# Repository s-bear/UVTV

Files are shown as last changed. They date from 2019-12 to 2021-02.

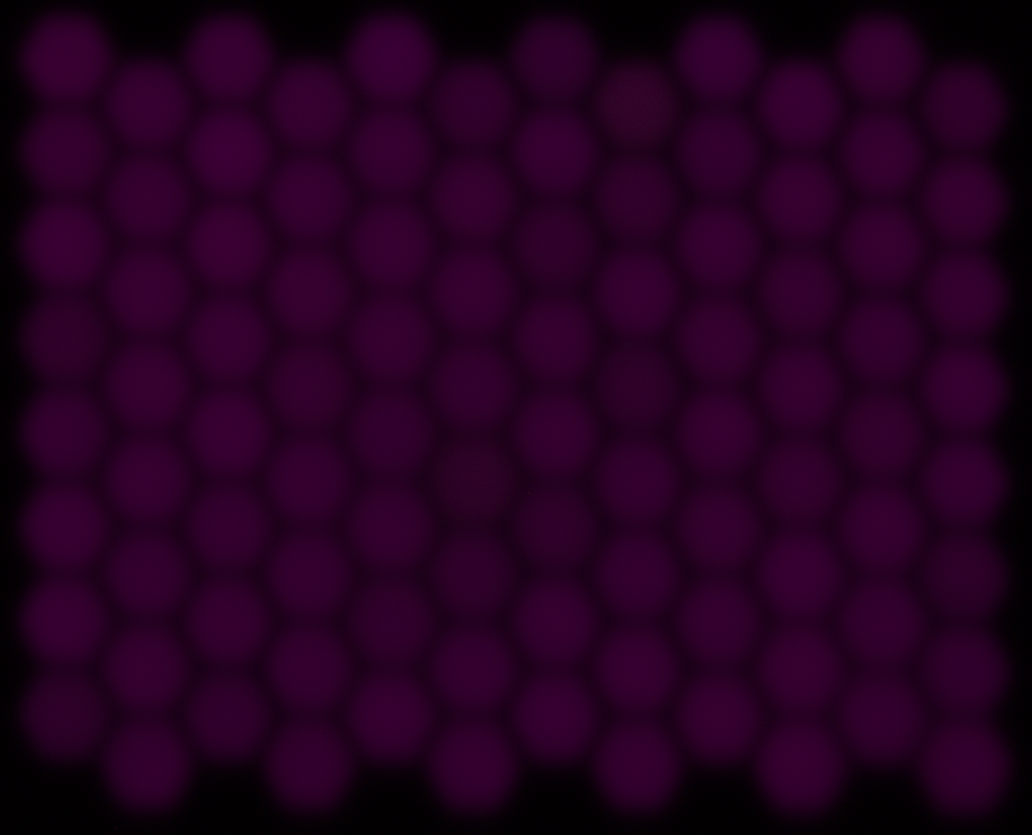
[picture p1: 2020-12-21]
software/scripts/board 2 data/uv_0.png

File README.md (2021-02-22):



# UVTV
RGB-V-UV LED display, as published in "A five-channel LED display to investigate UV perception" in Methods in Ecology and Evolution, 2021.

## TO DO
- Display: Compactness and seamless edge-to-edge display panelling is *not* a priority any more. There are a few places where these design goals made things quite difficult and any new production should have these changes made:
  - [ ] Point-of-Load power supply on display board for LEDs.
  - [ ] Separate LED power from TLC5955 power.
  - [ ] Increase margins and put mounting holes in sane places.
  - [ ] Use larger connectors for the flat-flex cables. Assess signal integrity and see if more conductors would be useful for shielding.
  - [ ] Another layer of PCB might be in order to ease routing of control signals, especially if there are signal integrity issues at higher speeds.
- Controller: A higher-speed controller is necessary to use the full potential of the display panel. There are several viable alternatives:
  1. A high-speed microcontroller module, such as the Teensy 4.1 (600 MHz), using built-in SPI or bit-banging to communicate with TLC5955 chips.
  2. A microcontroller + FPGA combo -- using the microcontroller to handle USB and FPGA to handle the TLC5955 communication.
  3. An FPGA to handle both USB and TLC5955.
- 3D Models
  - [ ] Redraw in an open source CAD tool, e.g. FreeCAD.

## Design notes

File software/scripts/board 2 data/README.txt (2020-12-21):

This is example flatfield calibration data from the 2nd UVTV board made.

The directories 0, 1, and 2 hold data captured before calibration (0) and 
after 1 and 2 iterations of the procedure respectively.

The "test_panel.py" script was run to show the "corners", "red", "green",
"blue", "violet", and "uv" images.
For the initial run, the script was configured with:
    reset_config = True
    save_config = False
    config_path = 'board 2 data/0'
Setting "reset_config = True" means the script generates "panel_config.npz" with
default data (lines 30-37).

Photos of the display were taken at each stage of the script using a modified
Olympus E-PL5 camera, the raw ORF files saved in 'board 2 data/0'.

The ORF files were converted to tiff using RawTherapee, with the settings
stored in the associated pp3 files. As the tiff files are too large for
github, you must generate them yourself using RawTherapee.

"pixel_stats.py" was run with
    config_path = 'board 2 data/0'
to generate "pixel_stats.npz"

"flatfield.py" was run with
    config_path = 'board 2 data/0'
to update "panel_config.npz" with new dotcorrect coefficients.

The procedure was then repeated again, running "test_panel.py" with
    reset_config = False
    save_config = False
    config_path = 'board 2 data/0'

The new images were saved into "board 2 data/1" and "0/panel_config.npz" was
copied to "1/panel_config.npz" so that "flatfield.py" could update it with new
coefficients.

The final round of images was generated using these coefficients and saved into
"board 2 data/2" for validation and to generate figures showing uniformity.

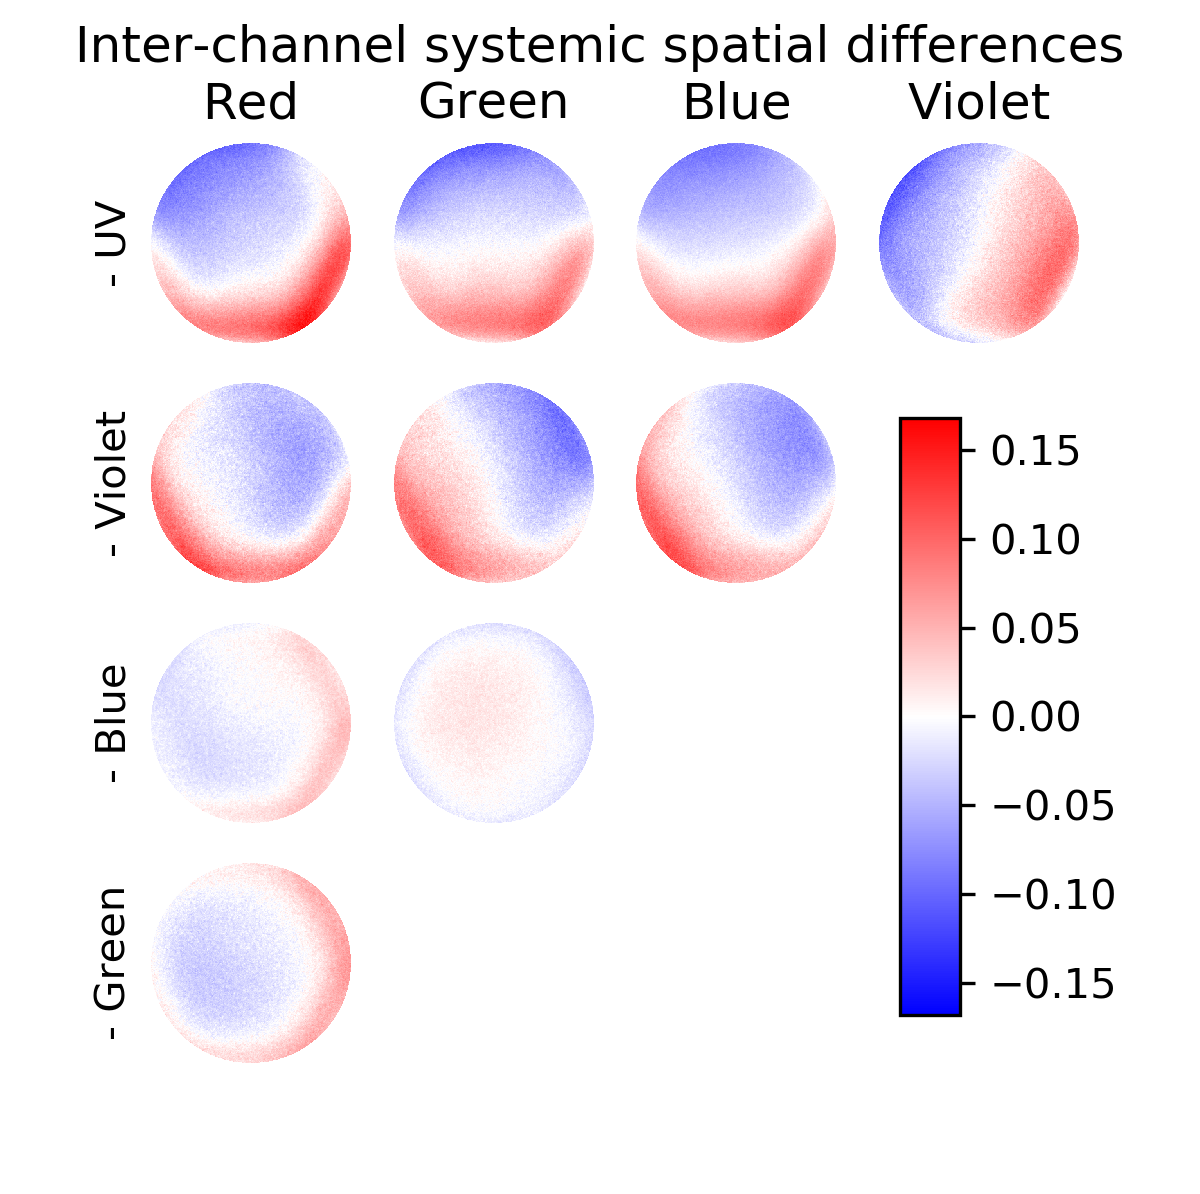
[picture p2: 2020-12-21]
software/scripts/board 2 data/spatial deviation.png

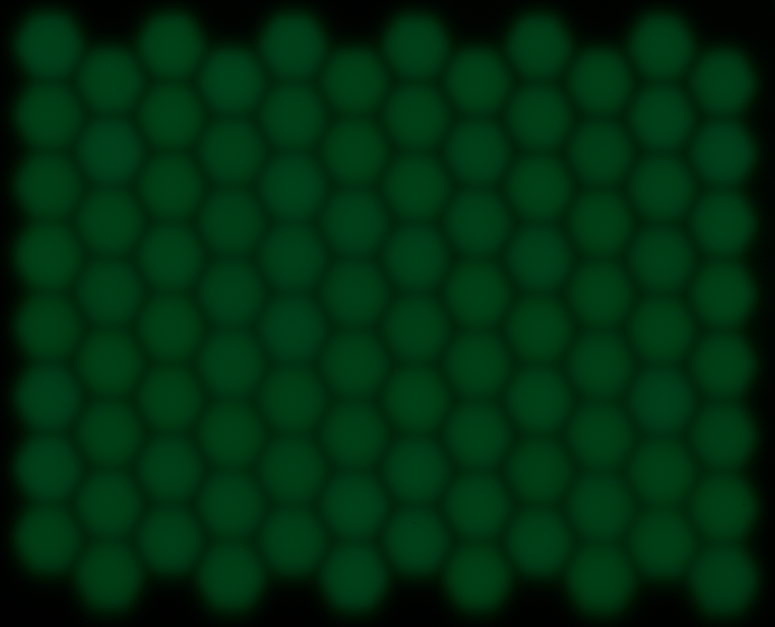
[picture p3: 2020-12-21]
software/scripts/board 2 data/green_0.png

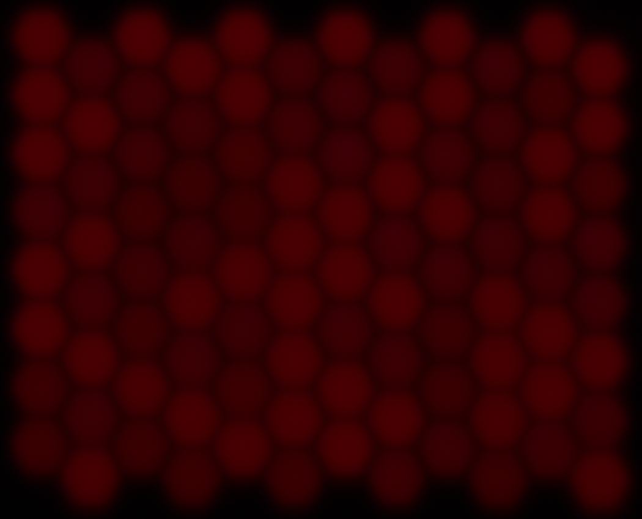
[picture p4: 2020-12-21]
software/scripts/board 2 data/red_0.png

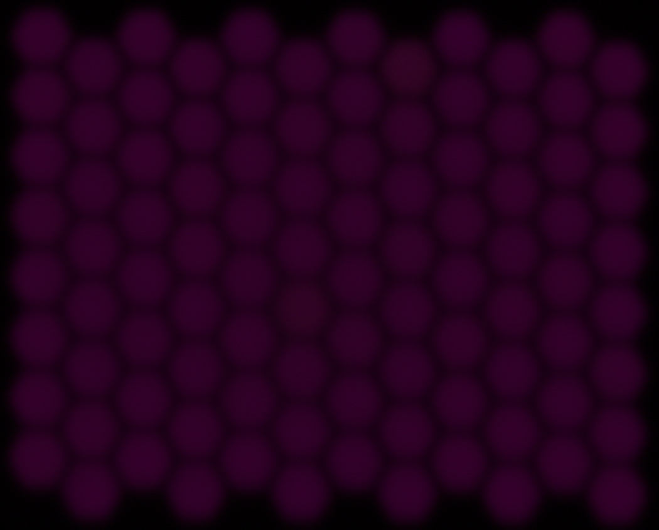
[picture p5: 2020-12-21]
software/scripts/board 2 data/uv_2.png

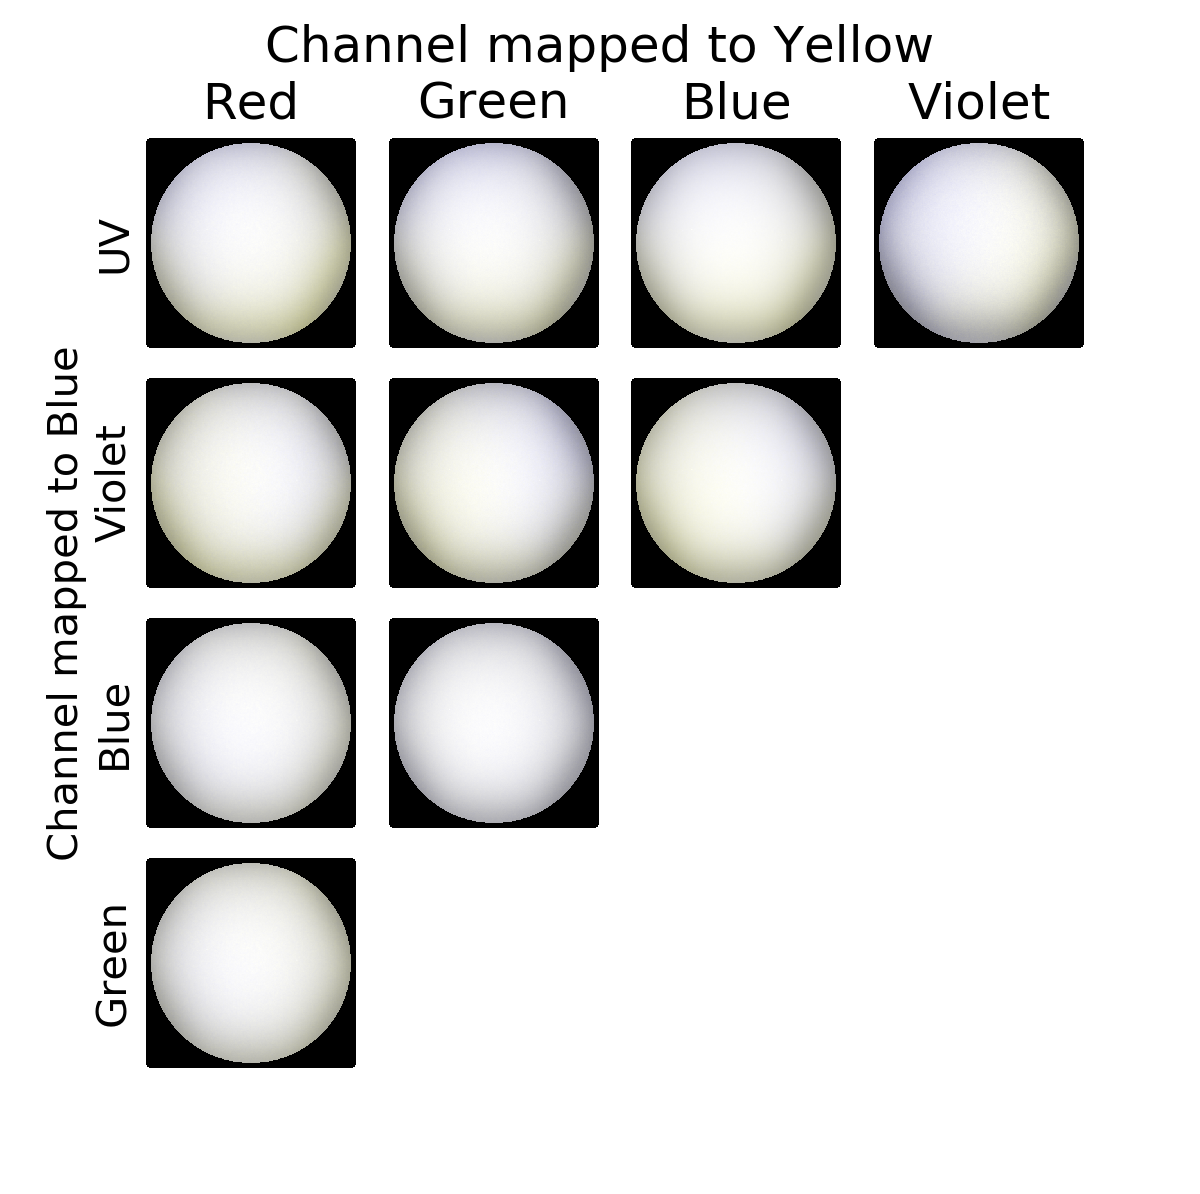
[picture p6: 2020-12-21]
software/scripts/board 2 data/spatial deviation 2.png

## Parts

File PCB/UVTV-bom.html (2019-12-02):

Ref | Count | Value | Library | Part | Footprint | Description | Vendor
C1 | 1 | 220u | Device | CP | Capacitor_Tantalum_SMD:CP_EIA-7343-31_Kemet-D_Pad2.25x2.55mm_HandSolder | Polarised capacitor
C2, C3 | 2 | 47u | Device | C | Capacitor_SMD:C_1206_3216Metric_Pad1.42x1.75mm_HandSolder | Unpolarized capacitor
C4 | 1 | 100u | Device | CP | Capacitor_Tantalum_SMD:CP_EIA-7343-31_Kemet-D_Pad2.25x2.55mm_HandSolder | Polarised capacitor
C[5:6] | 2 | 0.1u | Device | C | Capacitor_SMD:C_0603_1608Metric_Pad1.05x0.95mm_HandSolder | Unpolarized capacitor
J0 | 1 | Barrel_Jack | Connector | Barrel_Jack_MountingPin | Connector_BarrelJack:BarrelJack_CUI_PJ-063AH_Horizontal_CircularHoles | DC Barrel Jack with a mounting pin
J1 | 1 | Conn_01x08_Male | Connector | Conn_01x08_Male | Connector_PinHeader_2.54mm:PinHeader_1x08_P2.54mm_Vertical | Generic connector, single row, 01x08, script generated (kicad-library-utils/schlib/autogen/connector/)
Q0[A:B], Q1[A:B] | 4 | Q_NMOS_GSD | Device | Q_NMOS_GSD | Package_TO_SOT_SMD:SOT-23 | Transistor N-MOSFETwith substrate diode (general)
R1 | 1 | 348k | Device | R | Resistor_SMD:R_0603_1608Metric_Pad1.05x0.95mm_HandSolder | Resistor
R2 | 1 | 422 | Device | R | Resistor_SMD:R_0603_1608Metric_Pad1.05x0.95mm_HandSolder | Resistor
R[3:12] | 10 | 12Ω, 1W | Device | R | Resistor_THT:R_Axial_DIN0207_L6.3mm_D2.5mm_P10.16mm_Horizontal | Resistor
RGB[0:15] | 16 | LED_ARGB | Device | LED_ARGB | UVTV:EAST1616RGBA | LED RGB, common anode (pin 1)
U0 | 1 | LMZ3060x | UVTV | LMZ3060x | UVTV:Ti-S-PB1QFN-N39
U[1:2] | 2 | TLC5955-DCA | UVTV | TLC5955-DCA | Package_SO:HTSSOP-56-1EP_6.1x14mm_P0.5mm_EP3.61x6.35mm
UV[0:15] | 16 | LED | Device | LED | UVTV:D_0606_1616Metric | LED generic
V[0:15] | 16 | LED | Device | LED | LED_SMD:LED_0603_1608Metric | LED generic

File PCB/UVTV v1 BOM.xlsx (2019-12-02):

Source | G:\Sam\Projects\UV LED display\UVTV\UVTV.sch
Date | 2019-05-17
Tool | Eeschema (5.0.1)-3
Component count | 311
Ref | Count | Value | Voltage | Description | Manufacturer | Part # | Vendor | Order # | Note
~ | 1 |  |  | FFC cable 0.5mm, 15 POS, 152 mm long | Parlex USA LLC | 050R15-152B | Digikey | HFF-15U-06 | Other brands acceptable, length within 120-200 mm
C1A,C1B,C1C,C1D,C1E,C2A,C2B,C2C,C2D,C2E | 10 | 0.1u | 6V | Decoupling caps | Samsung | CL10F104ZO8NNNC | Digikey | 1276-1258 | Other brands acceptable
J1 | 1 |  |  | FFC connector | Hirose | FH19SC-15S-0.5SH(09) | Digikey | H125831
RGB1A0,RGB1A1,RGB1A2,RGB1A3,RGB1A4,RGB1A5,RGB1A6,RGB1A7,RGB1A8,RGB1A9,RGB1A10,RGB1A11,RGB1A12,RGB1A13,RGB1A14,RGB1A15,RGB1B0,RGB1B1,RGB1B2,RGB1B3,RGB1B4,RGB1B5,RGB1B6,RGB1B7,RGB1B8,RGB1B9,RGB1B10,RGB1B11,RGB1B12,RGB1B13,RGB1B14,RGB1B15,RGB1C0,RGB1C1,RGB1C2,RGB1C3,RGB1C4,RGB1C5,RGB1C6,RGB1C7,RGB1C8,RGB1C9,RGB1C10,RGB1C11,RGB1C12,RGB1C13,RGB1C14,RGB1C15,RGB2A0,RGB2A1,RGB2A2,RGB2A3,RGB2A4,RGB2A5,RGB2A6,RGB2A7,RGB2A8,RGB2A9,RGB2A10,RGB2A11,RGB2A12,RGB2A13,RGB2A14,RGB2A15,RGB2B0,RGB2B1,RGB2B2,RGB2B3,RGB2B4,RGB2B5,RGB2B6,RGB2B7,RGB2B8,RGB2B9,RGB2B10,RGB2B11,RGB2B12,RGB2B13,RGB2B14,RGB2B15,RGB2C0,RGB2C1,RGB2C2,RGB2C3,RGB2C4,RGB2C5,RGB2C6,RGB2C7,RGB2C8,RGB2C9,RGB2C10,RGB2C11,RGB2C12,RGB2C13,RGB2C14,RGB2C15 | 96 |  |  | RGB LEDs | Everlight Electronics Co Ltd | EAST1616RGBA3 | Digikey | 1080-1550
U-RGB1A,U-RGB2A,U-RGB1B,U-RGB2B,U-RGB1C,U-RGB2C,U-UV1A,U-UV2A,U-UV1C,U-UV2C | 10 |  |  | 3x16 CC LED controller | Texas Instruments | TLC5955RTQR | Digikey | 296-40588
UV1A0,UV1A1,UV1A2,UV1A3,UV1A4,UV1A5,UV1A6,UV1A7,UV1A8,UV1A9,UV1A10,UV1A11,UV1A12,UV1A13,UV1A14,UV1A15,UV1B0,UV1B1,UV1B2,UV1B3,UV1B4,UV1B5,UV1B6,UV1B7,UV1B8,UV1B9,UV1B10,UV1B11,UV1B12,UV1B13,UV1B14,UV1B15,UV1C0,UV1C1,UV1C2,UV1C3,UV1C4,UV1C5,UV1C6,UV1C7,UV1C8,UV1C9,UV1C10,UV1C11,UV1C12,UV1C13,UV1C14,UV1C15,UV2A0,UV2A1,UV2A2,UV2A3,UV2A4,UV2A5,UV2A6,UV2A7,UV2A8,UV2A9,UV2A10,UV2A11,UV2A12,UV2A13,UV2A14,UV2A15,UV2B0,UV2B1,UV2B2,UV2B3,UV2B4,UV2B5,UV2B6,UV2B7,UV2B8,UV2B9,UV2B10,UV2B11,UV2B12,UV2B13,UV2B14,UV2B15,UV2C0,UV2C1,UV2C2,UV2C3,UV2C4,UV2C5,UV2C6,UV2C7,UV2C8,UV2C9,UV2C10,UV2C11,UV2C12,UV2C13,UV2C14,UV2C15 | 96 |  |  | UV LED (365 nm) | Vishay Semiconductor Opto Division | VLMU1610-365-135 | Digikey | VLMU1610-365-135
V1A0,V1A1,V1A2,V1A3,V1A4,V1A5,V1A6,V1A7,V1A8,V1A9,V1A10,V1A11,V1A12,V1A13,V1A14,V1A15,V1B0,V1B1,V1B2,V1B3,V1B4,V1B5,V1B6,V1B7,V1B8,V1B9,V1B10,V1B11,V1B12,V1B13,V1B14,V1B15,V1C0,V1C1,V1C2,V1C3,V1C4,V1C5,V1C6,V1C7,V1C8,V1C9,V1C10,V1C11,V1C12,V1C13,V1C14,V1C15,V2A0,V2A1,V2A2,V2A3,V2A4,V2A5,V2A6,V2A7,V2A8,V2A9,V2A10,V2A11,V2A12,V2A13,V2A14,V2A15,V2B0,V2B1,V2B2,V2B3,V2B4,V2B5,V2B6,V2B7,V2B8,V2B9,V2B10,V2B11,V2B12,V2B13,V2B14,V2B15,V2C0,V2C1,V2C2,V2C3,V2C4,V2C5,V2C6,V2C7,V2C8,V2C9,V2C10,V2C11,V2C12,V2C13,V2C14,V2C15 | 96 |  |  | UV LED (395 nm) | Bivar Inc | SM0603UV-395 | Digikey | 492-1949

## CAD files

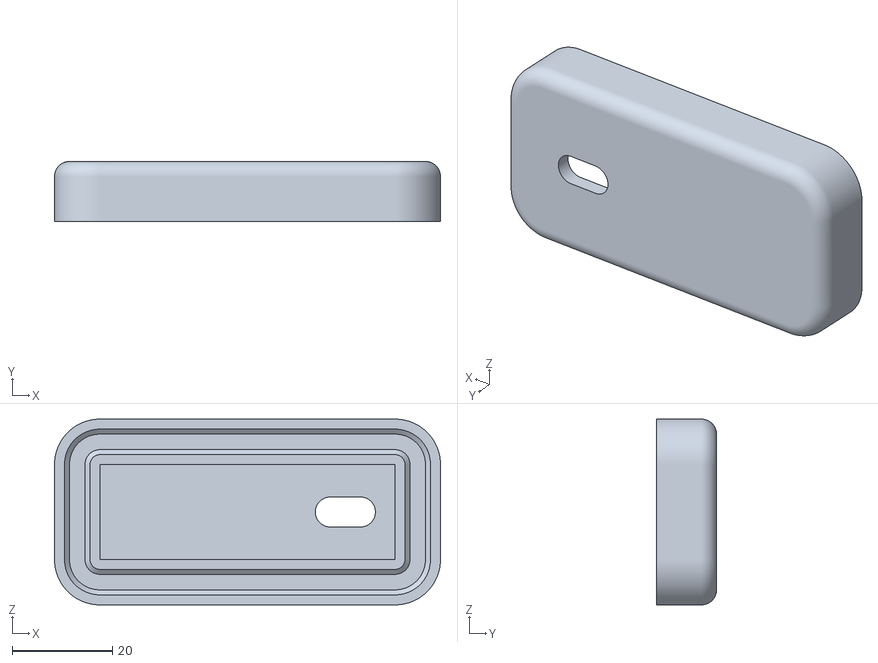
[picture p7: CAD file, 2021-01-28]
3D models/LED box top.stl
77.1 x 12.0 x 37.1

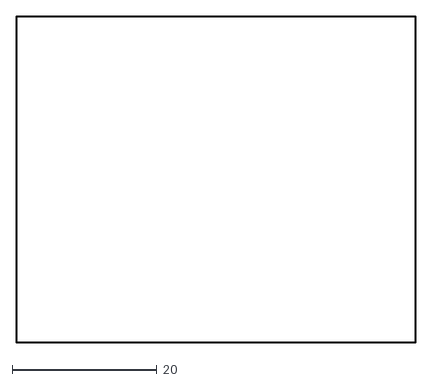
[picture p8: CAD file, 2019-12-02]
PCB/Gerbers/UVTV-Edge.Cuts.dxf
55.1 x 45.1

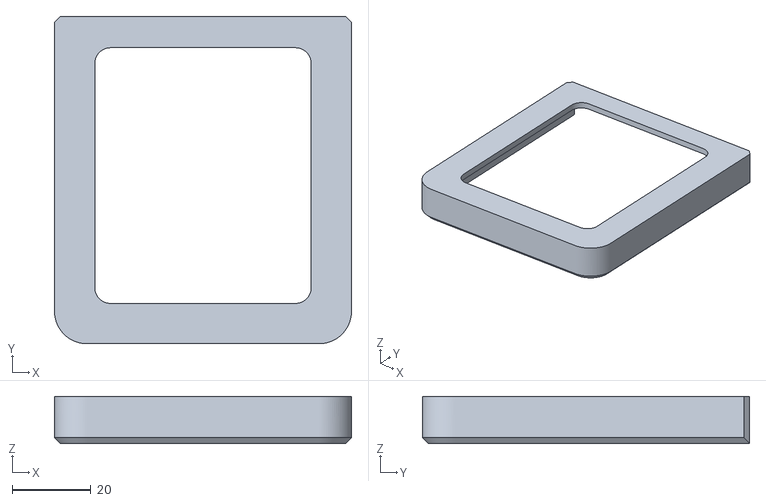
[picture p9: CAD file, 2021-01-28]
3D models/LED box bracket.stl
75.5 x 83.2 x 12.0

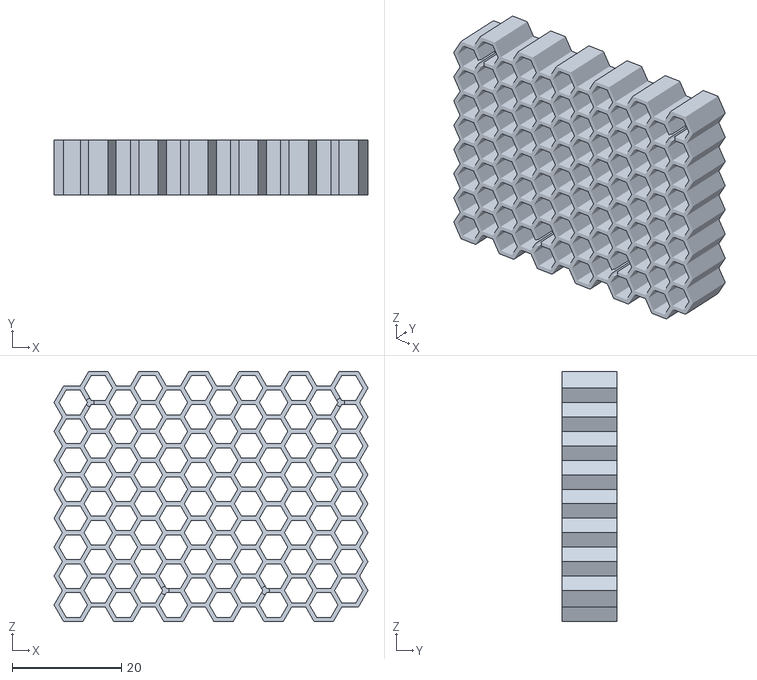
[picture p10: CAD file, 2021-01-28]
3D models/baffle.stl
57.5 x 10.0 x 45.8

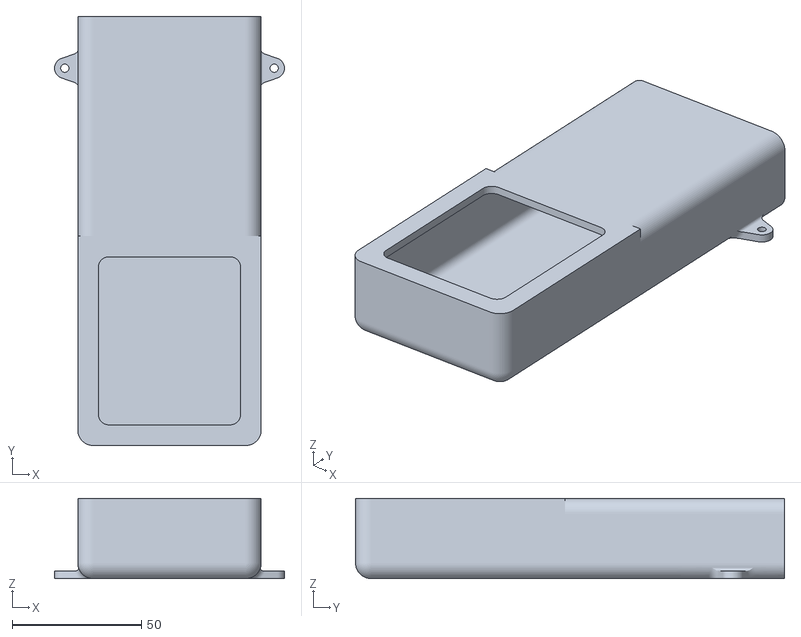
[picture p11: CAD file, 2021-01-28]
3D models/LED box.stl
89.0 x 166.0 x 31.0

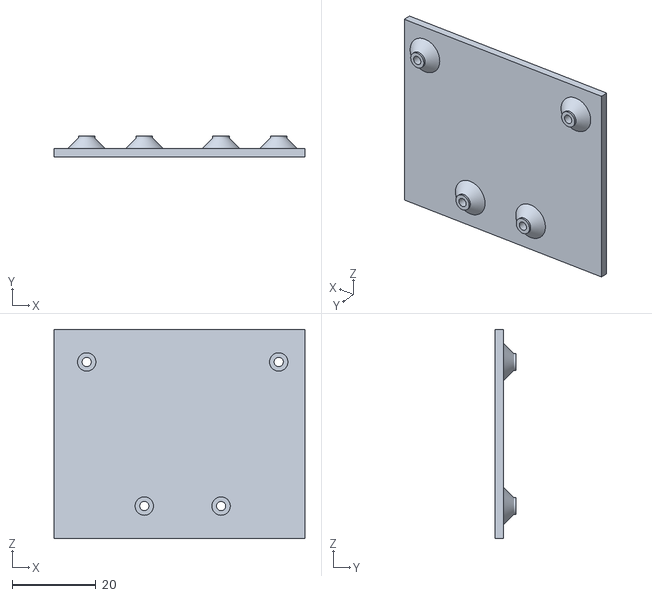
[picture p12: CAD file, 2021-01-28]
3D models/Panel mount plate.stl
60.0 x 5.00 x 50.0

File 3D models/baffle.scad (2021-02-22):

$fs = 0.1;

pitch = 5.3;
grid = [12,8];
wall = 0.8;
height = 10;

hole_dia = 1.5;
hole_depth = 5;

pitch_x = pitch*cos(30);
cell_w = pitch/cos(30);

hole_offsets = [
        [3*pitch_x + 0.5*cell_w, pitch/2],
        [7*pitch_x + 0.5*cell_w, pitch/2],
        [0.5*cell_w, 7*pitch],
        [10*pitch_x + 0.5*cell_w, 7*pitch]
    ];

module cylinder_outer(height,radius) {
    n = ($fn>0?($fn>=3?$fn:3):ceil(max(min(360/$fa,radius*2*PI/$fs),5)));
    cylinder(h=height,r=radius/cos(180/n),$fn=n);
}

module hex(h,w) {
    //w is across flats
    r = w*0.5773502691896257; // 1/(2*cos(180/6))
    cylinder(h,r,r,$fn=6);
}

module cell() {
    difference() {
        hex(height,pitch+wall);
        hex(height,pitch-wall);
    }
}

difference() {
    union() {
        for(ix = [0 : 2 : grid.x - 1]) {
            for(iy = [0 : grid.y - 1]) {
                translate([pitch_x*ix, pitch*iy]) cell();
                translate([pitch_x*(ix+1),pitch*(iy+0.5)]) cell();
            }
        }
    }

    for(xy = hole_offsets) {
        translate(xy)
        cylinder_outer(hole_depth,hole_dia/2);
    }
}

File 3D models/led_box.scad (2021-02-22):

$fs = 0.1;
tolerance = 1; //gap between parts

//main body parameters
window_size = [55,65];
interior_depth = 25;
flat_width = 10;
wall_thickness = 3;
tube_length = 85;

hole_offset = 20;
hole_pad_dia = 8;
hole_dia = 3.2;
tab_thickness = 5;

window_fillet = 3;
interior_fillet = 3;

//lid
lid_slot = [10, 15]; //diameter, length
lid_lip = 5;

//retainer
retainer_lip = 10;

//platform
platform_size = [50,60];
standoff_dia = 4;
platform_hole = [2.2,4.4,1.6]; //diameter, countersink diameter, countersink depth

pitch = 5.3;
grid = [8,12];

//computed parameters
exterior_fillet = interior_fillet+wall_thickness;
box_size = [window_size.x + 2*flat_width, window_size.y + 2*flat_width, interior_depth + 2*wall_thickness];
tube_size = [window_size.x+2*flat_width,interior_depth+2*wall_thickness,tube_length];

lid_size = [tube_size.x + 2*wall_thickness + tolerance, tube_size.y + 2*wall_thickness + tolerance, lid_lip + wall_thickness];
lid_fillet = exterior_fillet + wall_thickness + tolerance/2;

module square_rounded(size, radius, center = false) {
    offset(r = radius) {
        offset(delta = -radius) {
            square(size,center);
        }
    }
}

//from https://en.wikibooks.org/wiki/OpenSCAD_User_Manual/Other_Language_Features
function circle_edges(r) = ($fn>0?($fn>=3?$fn:3):ceil(max(min(360/$fa,r*2*PI/$fs),5)));

module circle_outer(radius) {
    //number of edges
    n = circle_edges(radius);
    circle(r=radius/cos(180/n),$fn=n);
}

module cylinder_outer(height,radius) {
    n = circle_edges(radius);
    cylinder(h=height,r=radius/cos(180/n),$fn=n);
}

module cube_rounded(size, radius) {
    dx = size.x/2 - radius;
    dy = size.y/2 - radius;
    dz = size.z/2 - radius;
    hull() {
        translate([-dx,-dy,-dz]) sphere(radius);
        translate([ dx,-dy,-dz]) sphere(radius);
        translate([-dx, dy,-dz]) sphere(radius);
        translate([ dx, dy,-dz]) sphere(radius);
        translate([-dx,-dy, dz]) sphere(radius);
        translate([ dx,-dy, dz]) sphere(radius);
        translate([-dx, dy, dz]) sphere(radius);
        translate([ dx, dy, dz]) sphere(radius);
    };
}

module window_box_shell(size, radius) {
    hull() {
        dx = size.x/2 - radius;
        dy = size.y/2 - radius;
        dz = size.z/2 - radius;
        translate([-dx,-dy,-dz]) sphere(radius);
        translate([ dx,-dy,-dz]) sphere(radius);
        translate([-dx, dy,-dz]) rotate([90,0,0]) cylinder(2*radius,r=radius,center=true);
        translate([ dx, dy,-dz]) rotate([90,0,0]) cylinder(2*radius,r=radius,center=true);
        translate([-dx,-dy, dz]) cylinder(2*radius,r=radius,center=true);
        translate([ dx,-dy, dz]) cylinder(2*radius,r=radius,center=true);
        translate([-dx, dy, dz]) rotate([90,0,0]) cube(2*radius,center=true);
        translate([ dx, dy, dz]) rotate([90,0,0]) cube(2*radius,center=true);
    };    
}


module window_box() {
    difference() {
        //outer shell
        window_box_shell(box_size, interior_fillet + wall_thickness);
        
        //cut away interior to leave walls
        translate([0,wall_thickness,0])
        cube_rounded(box_size - [2*wall_thickness,0,2*wall_thickness], interior_fillet);
        
        //cut the window out
        translate([0,0,box_size.z/2 - 0.5*wall_thickness])
        linear_extrude(1.1*wall_thickness,center=true) {
           square_rounded(window_size,window_fillet,true);
        }
    }
}

module mount_tab(x) {
    translate([x,0,0])
    difference() {
    //rounded triangle
        linear_extrude(tab_thickness) {
            translate([-hole_pad_dia,0,0])
            minkowski() {
                circle(d=hole_pad_dia);
                circle(d=2*hole_pad_dia, $fn=3);
            }
        }
        translate([0,0,-0.05])
        cylinder_outer(1.1*tab_thickness,hole_dia/2);
    }
}


module tube() {
    difference() {
        union() {
            //tube body
            linear_extrude(tube_size.z)
            square_rounded([tube_size.x,tube_size.y],exterior_fillet,center=true);
    
            translate([0, tube_size.y/2, tube_length - hole_offset]) rotate([90,0,0]) {
                mount_tab(tube_size.x/2 + hole_pad_dia/2);
                mirror([1,0,0]) mount_tab(tube_size.x/2 + hole_pad_dia/2);
            }
        }
        //remove tube interior
        translate([0,0,-0.05])
        linear_extrude(tube_size.z+0.1)
        square_rounded([tube_size.x - 2*wall_thickness,tube_size.y-2*wall_thickness],interior_fillet,center=true);
        }
}

module body() {
    union() {
        rotate([90,0,0])
        window_box();

        translate([0,0,0.5*window_size.y+flat_width])
        tube();
    }
}

module lid() {
    difference() {
        linear_extrude(lid_size.z)
        square_rounded([lid_size.x,lid_size.y],lid_fillet,true);
        
        translate([0,0,wall_thickness])
        linear_extrude(lid_size.z)
        square_rounded([lid_size.x-2*wall_thickness,lid_size.y-2*wall_thickness],lid_fillet-wall_thickness,true);
        
        translate([0,0,-0.05])
        hull() {
            dx = (lid_slot.y - lid_slot.x)/2;
            translate([dx,0,0]) cylinder(1.1*wall_thickness,d=lid_slot.x);
            translate([-dx,0,0]) cylinder(1.1*wall_thickness,d=lid_slot.x);
        }
    }
}

module retainer() {
    retainer_size = [box_size.x + 2*wall_thickness + tolerance, box_size.y + wall_thickness + tolerance/2, wall_thickness + retainer_lip];
    
    shell_size = [retainer_size.x, retainer_size.y, box_size.z];
    difference() {
        translate([0, 1.25*tolerance-wall_thickness, 0])
        window_box_shell(shell_size, interior_fillet + 2*wall_thickness + tolerance/2);
        
        translate([0,0,-retainer_size.z])
        scale([1.1,1.1,1])
        cube(shell_size,true);
        
        //cut the window box out
        color("orange")
        translate([0,0,-wall_thickness])
        window_box_shell([box_size.x+tolerance,box_size.y+tolerance,box_size.z], interior_fillet + wall_thickness + tolerance/2);
        
        //cut the window out
        translate([0,0,box_size.z/2 - 0.5*wall_thickness])
        linear_extrude(1.1*wall_thickness,center=true) {
           square_rounded(window_size,window_fillet,true);
        }
    }
}

module standoff(h, d, off,slope) {
    r = d/2;
    union() {
        cylinder(h,r,r);
        cylinder(h-off,r+slope*(h-off),r);
    }
}

module countersink(depth,drill_dia,sink_dia,sink_depth) {
    union() {
        cylinder_outer(depth,drill_dia/2);
        cylinder_outer(sink_depth,sink_dia/2);
    }
}

module platform() {
    pitch_y = pitch*cos(30);
    cell_h = pitch/cos(30);
    
    t = wall_thickness;
    d = standoff_dia;
    
    led_origin = [-(grid.x-0.5)*pitch/2, -(grid.y - 1)*pitch_y/2];
    hole_offsets = [
        [pitch/2, 3*pitch_y + 0.5*cell_h],
        [pitch/2, 7*pitch_y + 0.5*cell_h],
        [7*pitch, 0.5*cell_h],
        [7*pitch, 10*pitch_y + 0.5*cell_h]
    ];
    
    difference() {
        union() {
            linear_extrude(t)
            square_rounded(platform_size,interior_fillet,center=true);
        
            translate([led_origin.x, led_origin.y, t]) {
                for(xy = hole_offsets) translate(xy) standoff(t,d,1,1);
            }
        }
        translate(led_origin) {
            for(xy = hole_offsets) translate(xy) countersink(2*t,platform_hole.x,platform_hole.y,platform_hole.z);
        }
    }
}

body();

translate([0,0, 0.5*window_size.y + flat_width + tube_length + wall_thickness])
rotate([180,0,0])
lid();

translate([0,-wall_thickness,0])
rotate([90,0,0])
retainer();

rotate([90,0,0])
platform();

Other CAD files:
3D models/LED box bracket.ipt
3D models/LED box top.ipt
3D models/LED box.ipt
3D models/Panel mount plate.ipt
3D models/baffle.ipt
PCB/Gerbers/UVTV-B.SilkS.dxf
PCB/Gerbers/UVTV-F.SilkS.dxf

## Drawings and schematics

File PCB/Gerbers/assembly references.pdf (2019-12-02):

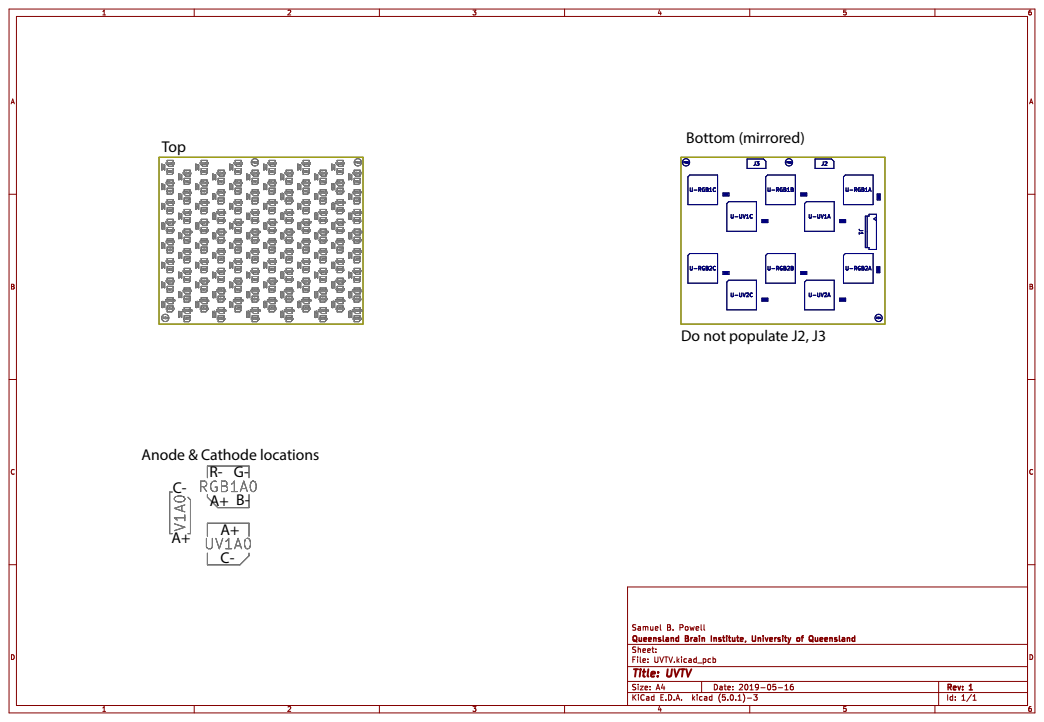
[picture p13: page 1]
Top; Bottom (mirrored); Anode & Cathode locations

Do not populate J2, J3

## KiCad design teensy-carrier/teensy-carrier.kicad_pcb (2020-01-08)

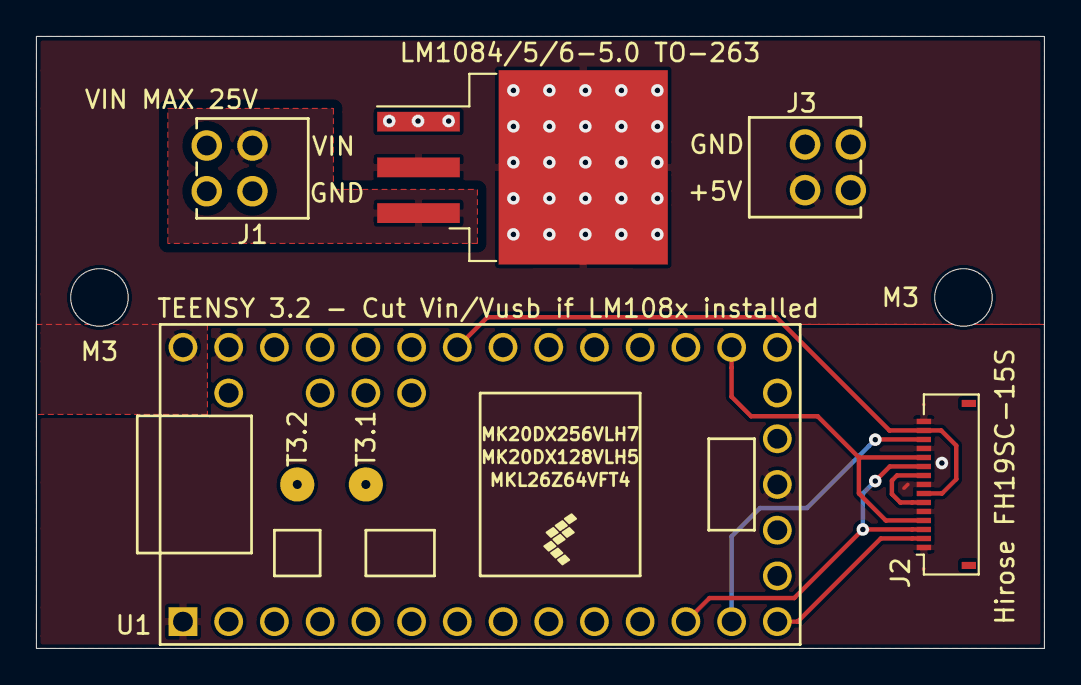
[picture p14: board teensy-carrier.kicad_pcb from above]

Board: 2 copper layers, 56.0 x 34.0 mm, 5 parts (0 on the bottom side), 9 nets.

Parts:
J1: Conn_01x02_Male; TerminalBlock_DECA-MB312-254-2
J2: Conn_01x15_Female; Hirose_FH19SC-15S-0.5SH_1x15-1MP_P0.50mm_Horizontal
J3: Conn_01x02_Female; TerminalBlock_DECA-MB312-254-2
U1: Teensy3.2; Teensy30_31_32_LC
U2: LM1084-5.0; TO-263-3_TabPin2

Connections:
+5V: J3.2, U1.33, U2.2
/GCLK: J2.7, J2.14, U1.27
/LAT: J2.3, J2.10, U1.12
/SCLK: J2.4, J2.11, U1.21
/SIN1: J2.13, U1.13
/SOUT1_SIN2: J2.6, J2.9
/SOUT2: J2.2, U1.14
GND: J1.1, J2.1, J2.5, J2.8, J2.12, J2.15, J3.1, U1.1, U1.17, U1.32, U2.1
unnamed: J1.2, U2.3

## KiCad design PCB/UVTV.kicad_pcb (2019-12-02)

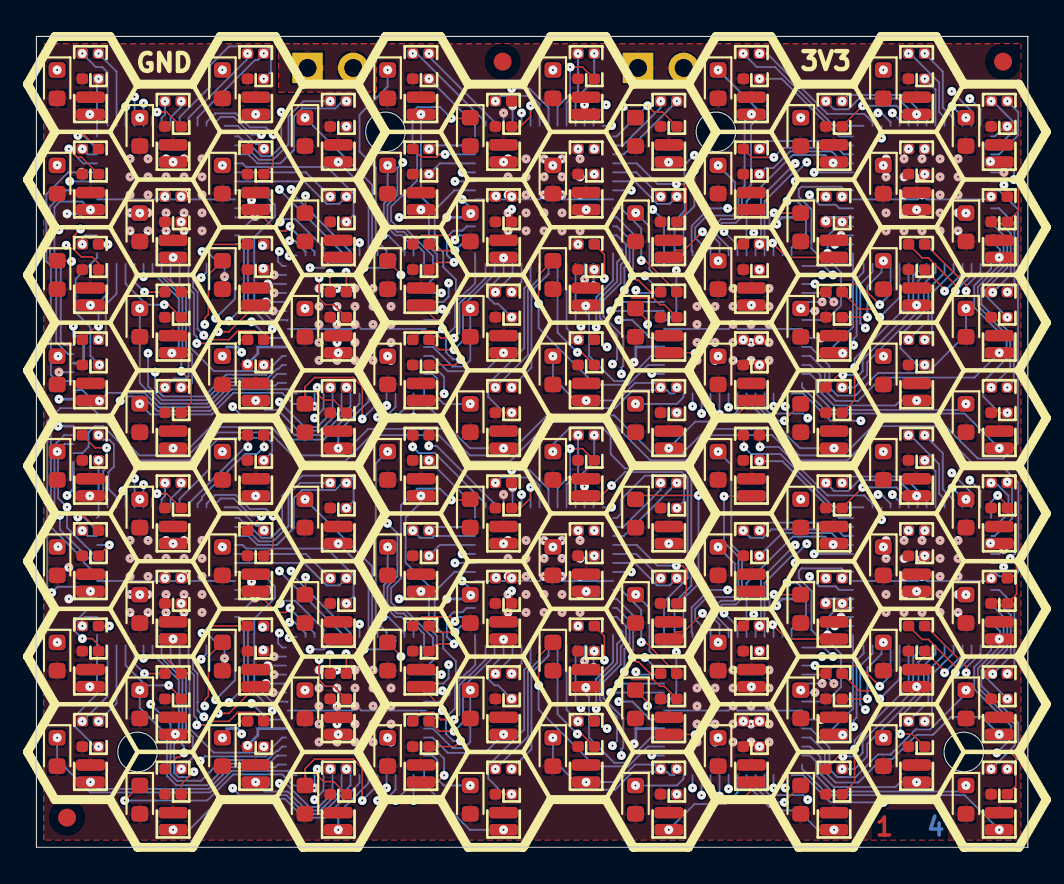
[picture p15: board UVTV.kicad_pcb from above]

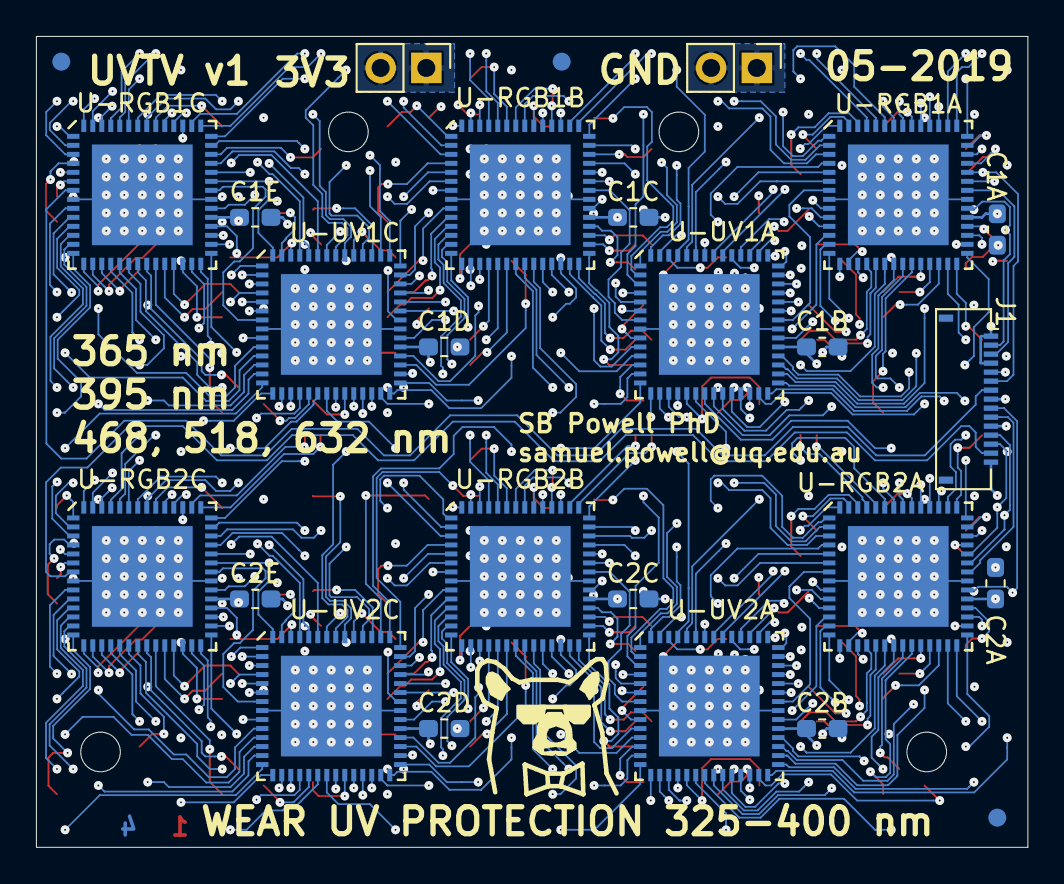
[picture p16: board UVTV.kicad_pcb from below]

Board: 4 copper layers, 55.1 x 45.0 mm, 321 parts (26 on the bottom side), 500 nets.

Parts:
C1A, C1B, C1C, C1D, C1E, C2A, C2B, C2C, C2D, C2E: 0.1u; C_0603_1608Metric_Pad1.05x0.95mm_HandSolder
FID1, FID2, FID3, FID4, FID5, FID6: Fiducial_1mm_Dia_2mm_Outer
J1: Conn_01x15; Hirose_FH19SC-15S-0.5SH_1x15-1MP_P0.50mm_Horizontal
J2: Conn_01x02; PinHeader_1x02_P2.54mm_Vertical
J3: Conn_01x03; PinHeader_1x02_P2.54mm_Vertical
MH1A, MH1B, MH2A, MH2B: MountingHole; MountingHole_2.2mm_M2
RGB1A0, RGB1A1, RGB1A2, RGB1A3, RGB1A4, RGB1A5, RGB1A6, RGB1A7, RGB1A8, RGB1A9, RGB1A10, RGB1A11, RGB1A12, RGB1A13, RGB1A14, RGB1A15, RGB1B0, RGB1B1, RGB1B2, RGB1B3, RGB1B4, RGB1B5, RGB1B6, RGB1B7, RGB1B8, RGB1B9, RGB1B10, RGB1B11, RGB1B12, RGB1B13, RGB1B14, RGB1B15, RGB1C0, RGB1C1, RGB1C2, RGB1C3, RGB1C4, RGB1C5, RGB1C6, RGB1C7, RGB1C8, RGB1C9, RGB1C10, RGB1C11, RGB1C12, RGB1C13, RGB1C14, RGB1C15, RGB2A0, RGB2A1, RGB2A2, RGB2A3, RGB2A4, RGB2A5, RGB2A6, RGB2A7, RGB2A8, RGB2A9, RGB2A10, RGB2A11, RGB2A12, RGB2A13, RGB2A14, RGB2A15, RGB2B0, RGB2B1, RGB2B2, RGB2B3, RGB2B4, RGB2B5, RGB2B6, RGB2B7, RGB2B8, RGB2B9, RGB2B10, RGB2B11, RGB2B12, RGB2B13, RGB2B14, RGB2B15, RGB2C0, RGB2C1, RGB2C2, RGB2C3, RGB2C4, RGB2C5, RGB2C6, RGB2C7, RGB2C8, RGB2C9, RGB2C10, RGB2C11, RGB2C12, RGB2C13, RGB2C14, RGB2C15: EAST1616RGB; EAST1616RGBA
U-RGB1A, U-RGB1B, U-RGB1C, U-RGB2A, U-RGB2B, U-RGB2C: TLC5955-RTQ; QFN-56-1EP_8x8mm_P0.5mm_EP5.6x5.6mm
U-UV1A, U-UV1C, U-UV2A, U-UV2C: TLC5955-RTQ; QFN-56-1EP_8x8mm_P0.5mm_EP5.6x5.6mm
UV1A0, UV1A1, UV1A2, UV1A3, UV1A4, UV1A5, UV1A6, UV1A7, UV1A8, UV1A9, UV1A10, UV1A11, UV1A12, UV1A13, UV1A14, UV1A15, UV1B0, UV1B1, UV1B2, UV1B3, UV1B4, UV1B5, UV1B6, UV1B7, UV1B8, UV1B9, UV1B10, UV1B11, UV1B12, UV1B13, UV1B14, UV1B15, UV1C0, UV1C1, UV1C2, UV1C3, UV1C4, UV1C5, UV1C6, UV1C7, UV1C8, UV1C9, UV1C10, UV1C11, UV1C12, UV1C13, UV1C14, UV1C15, UV2A0, UV2A1, UV2A2, UV2A3, UV2A4, UV2A5, UV2A6, UV2A7, UV2A8, UV2A9, UV2A10, UV2A11, UV2A12, UV2A13, UV2A14, UV2A15, UV2B0, UV2B1, UV2B2, UV2B3, UV2B4, UV2B5, UV2B6, UV2B7, UV2B8, UV2B9, UV2B10, UV2B11, UV2B12, UV2B13, UV2B14, UV2B15, UV2C0, UV2C1, UV2C2, UV2C3, UV2C4, UV2C5, UV2C6, UV2C7, UV2C8, UV2C9, UV2C10, UV2C11, UV2C12, UV2C13, UV2C14, UV2C15: VLMU1610-365; D_0606_1616Metric
V1A0, V1A1, V1A2, V1A3, V1A4, V1A5, V1A6, V1A7, V1A8, V1A9, V1A10, V1A11, V1A12, V1A13, V1A14, V1A15, V1B0, V1B1, V1B2, V1B3, V1B4, V1B5, V1B6, V1B7, V1B8, V1B9, V1B10, V1B11, V1B12, V1B13, V1B14, V1B15, V1C0, V1C1, V1C2, V1C3, V1C4, V1C5, V1C6, V1C7, V1C8, V1C9, V1C10, V1C11, V1C12, V1C13, V1C14, V1C15, V2A0, V2A1, V2A2, V2A3, V2A4, V2A5, V2A6, V2A7, V2A8, V2A9, V2A10, V2A11, V2A12, V2A13, V2A14, V2A15, V2B0, V2B1, V2B2, V2B3, V2B4, V2B5, V2B6, V2B7, V2B8, V2B9, V2B10, V2B11, V2B12, V2B13, V2B14, V2B15, V2C0, V2C1, V2C2, V2C3, V2C4, V2C5, V2C6, V2C7, V2C8, V2C9, V2C10, V2C11, V2C12, V2C13, V2C14, V2C15: SM0603UV-395; LED_0603_1608Metric

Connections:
+3V3: C1A.1, C1B.1, C1C.1, C1D.1, C1E.1, C2A.1, C2B.1, C2C.1, C2D.1, C2E.1, J3.1, J3.2, RGB1A0.3, RGB1A1.3, RGB1A2.3, RGB1A3.3, RGB1A4.3, RGB1A5.3, RGB1A6.3, RGB1A7.3, RGB1A8.3, RGB1A9.3, RGB1A10.3, RGB1A11.3, RGB1A12.3, RGB1A13.3, RGB1A14.3, RGB1A15.3, RGB1B0.3, RGB1B1.3, RGB1B2.3, RGB1B3.3, RGB1B4.3, RGB1B5.3, RGB1B6.3, RGB1B7.3, RGB1B8.3, RGB1B9.3, RGB1B10.3, RGB1B11.3, RGB1B12.3, RGB1B13.3, RGB1B14.3, RGB1B15.3, RGB1C0.3, RGB1C1.3, RGB1C2.3, RGB1C3.3, RGB1C4.3, RGB1C5.3, RGB1C6.3, RGB1C7.3, RGB1C8.3, RGB1C9.3, RGB1C10.3, RGB1C11.3, RGB1C12.3, RGB1C13.3, RGB1C14.3, RGB1C15.3, RGB2A0.3, RGB2A1.3, RGB2A2.3, RGB2A3.3, RGB2A4.3, RGB2A5.3, RGB2A6.3, RGB2A7.3, RGB2A8.3, RGB2A9.3, RGB2A10.3, RGB2A11.3, RGB2A12.3, RGB2A13.3, RGB2A14.3, RGB2A15.3, RGB2B0.3, RGB2B1.3, RGB2B2.3, RGB2B3.3, RGB2B4.3, RGB2B5.3, RGB2B6.3, RGB2B7.3, RGB2B8.3, RGB2B9.3, RGB2B10.3, RGB2B11.3, RGB2B12.3, RGB2B13.3, RGB2B14.3, RGB2B15.3, RGB2C0.3, RGB2C1.3, RGB2C2.3, RGB2C3.3, RGB2C4.3, RGB2C5.3, RGB2C6.3, RGB2C7.3, RGB2C8.3, RGB2C9.3, RGB2C10.3, RGB2C11.3, RGB2C12.3, RGB2C13.3, RGB2C14.3, RGB2C15.3, U-RGB1A.33, U-RGB1B.33, U-RGB1C.33, U-RGB2A.33, U-RGB2B.33, U-RGB2C.33, U-UV1A.33, U-UV1C.33, U-UV2A.33, U-UV2C.33, UV1A0.2, UV1A1.2, UV1A2.2, UV1A3.2, UV1A4.2, UV1A5.2, UV1A6.2, UV1A7.2, UV1A8.2, UV1A9.2, UV1A10.2, UV1A11.2, UV1A12.2, UV1A13.2, UV1A14.2, UV1A15.2, UV1B0.2, UV1B1.2, UV1B2.2, UV1B3.2, UV1B4.2, UV1B5.2, UV1B6.2, UV1B7.2, UV1B8.2, UV1B9.2, UV1B10.2, UV1B11.2, UV1B12.2, UV1B13.2, UV1B14.2, UV1B15.2, UV1C0.2, UV1C1.2, UV1C2.2, UV1C3.2, UV1C4.2, UV1C5.2, UV1C6.2, UV1C7.2, UV1C8.2, UV1C9.2, UV1C10.2, UV1C11.2, UV1C12.2, UV1C13.2, UV1C14.2, UV1C15.2, UV2A0.2, UV2A1.2, UV2A2.2, UV2A3.2, UV2A4.2, UV2A5.2, UV2A6.2, UV2A7.2, UV2A8.2, UV2A9.2, UV2A10.2, UV2A11.2, UV2A12.2, UV2A13.2, UV2A14.2, UV2A15.2, UV2B0.2, UV2B1.2, UV2B2.2, UV2B3.2, UV2B4.2, UV2B5.2, UV2B6.2, UV2B7.2, UV2B8.2, UV2B9.2, UV2B10.2, UV2B11.2, UV2B12.2, UV2B13.2, UV2B14.2, UV2B15.2, UV2C0.2, UV2C1.2, UV2C2.2, UV2C3.2, UV2C4.2, UV2C5.2, UV2C6.2, UV2C7.2, UV2C8.2, UV2C9.2, UV2C10.2, UV2C11.2, UV2C12.2, UV2C13.2, UV2C14.2, UV2C15.2, V1A0.2, V1A1.2, V1A2.2, V1A3.2, V1A4.2, V1A5.2, V1A6.2, V1A7.2, V1A8.2, V1A9.2, V1A10.2, V1A11.2, V1A12.2, V1A13.2, V1A14.2, V1A15.2, V1B0.2, V1B1.2, V1B2.2, V1B3.2, V1B4.2, V1B5.2, V1B6.2, V1B7.2, V1B8.2, V1B9.2, V1B10.2, V1B11.2, V1B12.2, V1B13.2, V1B14.2, V1B15.2, V1C0.2, V1C1.2, V1C2.2, V1C3.2, V1C4.2, V1C5.2, V1C6.2, V1C7.2, V1C8.2, V1C9.2, V1C10.2, V1C11.2, V1C12.2, V1C13.2, V1C14.2, V1C15.2, V2A0.2, V2A1.2, V2A2.2, V2A3.2, V2A4.2, V2A5.2, V2A6.2, V2A7.2, V2A8.2, V2A9.2, V2A10.2, V2A11.2, V2A12.2, V2A13.2, V2A14.2, V2A15.2, V2B0.2, V2B1.2, V2B2.2, V2B3.2, V2B4.2, V2B5.2, V2B6.2, V2B7.2, V2B8.2, V2B9.2, V2B10.2, V2B11.2, V2B12.2, V2B13.2, V2B14.2, V2B15.2, V2C0.2, V2C1.2, V2C2.2, V2C3.2, V2C4.2, V2C5.2, V2C6.2, V2C7.2, V2C8.2, V2C9.2, V2C10.2, V2C11.2, V2C12.2, V2C13.2, V2C14.2, V2C15.2
/B1A0: RGB1A0.1, U-RGB1A.42
/B1A1: RGB1A1.1, U-RGB1A.48
/B1A2: RGB1A2.1, U-RGB1A.51
/B1A3: RGB1A3.1, U-RGB1A.1
/B1A4: RGB1A4.1, U-RGB1A.39
/B1A5: RGB1A5.1, U-RGB1A.45
/B1A6: RGB1A6.1, U-RGB1A.54
/B1A7: RGB1A7.1, U-RGB1A.4
/B1A8: RGB1A8.1, U-RGB1A.32
/B1A9: RGB1A9.1, U-RGB1A.26
/B1A10: RGB1A10.1, U-RGB1A.17
/B1A11: RGB1A11.1, U-RGB1A.11
/B1A12: RGB1A12.1, U-RGB1A.29
/B1A13: RGB1A13.1, U-RGB1A.23
/B1A14: RGB1A14.1, U-RGB1A.20
/B1A15: RGB1A15.1, U-RGB1A.14
/B1B0: RGB1B0.1, U-RGB1B.42
/B1B1: RGB1B1.1, U-RGB1B.48
/B1B2: RGB1B2.1, U-RGB1B.51
/B1B3: RGB1B3.1, U-RGB1B.1
/B1B4: RGB1B4.1, U-RGB1B.39
/B1B5: RGB1B5.1, U-RGB1B.45
/B1B6: RGB1B6.1, U-RGB1B.54
/B1B7: RGB1B7.1, U-RGB1B.4
/B1B8: RGB1B8.1, U-RGB1B.32
/B1B9: RGB1B9.1, U-RGB1B.26
/B1B10: RGB1B10.1, U-RGB1B.17
/B1B11: RGB1B11.1, U-RGB1B.11
/B1B12: RGB1B12.1, U-RGB1B.29
/B1B13: RGB1B13.1, U-RGB1B.23
/B1B14: RGB1B14.1, U-RGB1B.20
/B1B15: RGB1B15.1, U-RGB1B.14
/B1C0: RGB1C0.1, U-RGB1C.42
/B1C1: RGB1C1.1, U-RGB1C.48
/B1C2: RGB1C2.1, U-RGB1C.51
/B1C3: RGB1C3.1, U-RGB1C.1
/B1C4: RGB1C4.1, U-RGB1C.39
/B1C5: RGB1C5.1, U-RGB1C.45
/B1C6: RGB1C6.1, U-RGB1C.54
/B1C7: RGB1C7.1, U-RGB1C.4
/B1C8: RGB1C8.1, U-RGB1C.32
/B1C9: RGB1C9.1, U-RGB1C.26
/B1C10: RGB1C10.1, U-RGB1C.17
/B1C11: RGB1C11.1, U-RGB1C.11
/B1C12: RGB1C12.1, U-RGB1C.29
/B1C13: RGB1C13.1, U-RGB1C.23
/B1C14: RGB1C14.1, U-RGB1C.20
/B1C15: RGB1C15.1, U-RGB1C.14
/B2A0: RGB2A0.1, U-RGB2A.42
/B2A1: RGB2A1.1, U-RGB2A.48
/B2A2: RGB2A2.1, U-RGB2A.51
/B2A3: RGB2A3.1, U-RGB2A.1
/B2A4: RGB2A4.1, U-RGB2A.39
/B2A5: RGB2A5.1, U-RGB2A.45
/B2A6: RGB2A6.1, U-RGB2A.54
/B2A7: RGB2A7.1, U-RGB2A.4
/B2A8: RGB2A8.1, U-RGB2A.32
/B2A9: RGB2A9.1, U-RGB2A.26
/B2A10: RGB2A10.1, U-RGB2A.17
/B2A11: RGB2A11.1, U-RGB2A.11
/B2A12: RGB2A12.1, U-RGB2A.29
/B2A13: RGB2A13.1, U-RGB2A.23
/B2A14: RGB2A14.1, U-RGB2A.20
/B2A15: RGB2A15.1, U-RGB2A.14
/B2B0: RGB2B0.1, U-RGB2B.42
/B2B1: RGB2B1.1, U-RGB2B.48
/B2B2: RGB2B2.1, U-RGB2B.51
/B2B3: RGB2B3.1, U-RGB2B.1
/B2B4: RGB2B4.1, U-RGB2B.39
/B2B5: RGB2B5.1, U-RGB2B.45
/B2B6: RGB2B6.1, U-RGB2B.54
/B2B7: RGB2B7.1, U-RGB2B.4
/B2B8: RGB2B8.1, U-RGB2B.32
/B2B9: RGB2B9.1, U-RGB2B.26
/B2B10: RGB2B10.1, U-RGB2B.17
/B2B11: RGB2B11.1, U-RGB2B.11
/B2B12: RGB2B12.1, U-RGB2B.29
/B2B13: RGB2B13.1, U-RGB2B.23
/B2B14: RGB2B14.1, U-RGB2B.20
/B2B15: RGB2B15.1, U-RGB2B.14
/B2C0: RGB2C0.1, U-RGB2C.42
/B2C1: RGB2C1.1, U-RGB2C.48
/B2C2: RGB2C2.1, U-RGB2C.51
/B2C3: RGB2C3.1, U-RGB2C.1
/B2C4: RGB2C4.1, U-RGB2C.39
/B2C5: RGB2C5.1, U-RGB2C.45
/B2C6: RGB2C6.1, U-RGB2C.54
/B2C7: RGB2C7.1, U-RGB2C.4
/B2C8: RGB2C8.1, U-RGB2C.32
/B2C9: RGB2C9.1, U-RGB2C.26
/B2C10: RGB2C10.1, U-RGB2C.17
/B2C11: RGB2C11.1, U-RGB2C.11
/B2C12: RGB2C12.1, U-RGB2C.29
/B2C13: RGB2C13.1, U-RGB2C.23
/B2C14: RGB2C14.1, U-RGB2C.20
/B2C15: RGB2C15.1, U-RGB2C.14
/G1A0: RGB1A0.2, U-RGB1A.44
/G1A1: RGB1A1.2, U-RGB1A.50
/G1A2: RGB1A2.2, U-RGB1A.53
/G1A3: RGB1A3.2, U-RGB1A.3
/G1A4: RGB1A4.2, U-RGB1A.41
/G1A5: RGB1A5.2, U-RGB1A.47
/G1A6: RGB1A6.2, U-RGB1A.56
/G1A7: RGB1A7.2, U-RGB1A.6
/G1A8: RGB1A8.2, U-RGB1A.30
/G1A9: RGB1A9.2, U-RGB1A.24
/G1A10: RGB1A10.2, U-RGB1A.15
/G1A11: RGB1A11.2, U-RGB1A.9
/G1A12: RGB1A12.2, U-RGB1A.27
/G1A13: RGB1A13.2, U-RGB1A.21
/G1A14: RGB1A14.2, U-RGB1A.18
/G1A15: RGB1A15.2, U-RGB1A.12
/G1B0: RGB1B0.2, U-RGB1B.44
/G1B1: RGB1B1.2, U-RGB1B.50
/G1B2: RGB1B2.2, U-RGB1B.53
/G1B3: RGB1B3.2, U-RGB1B.3
/G1B4: RGB1B4.2, U-RGB1B.41
/G1B5: RGB1B5.2, U-RGB1B.47
/G1B6: RGB1B6.2, U-RGB1B.56
/G1B7: RGB1B7.2, U-RGB1B.6
/G1B8: RGB1B8.2, U-RGB1B.30
/G1B9: RGB1B9.2, U-RGB1B.24
/G1B10: RGB1B10.2, U-RGB1B.15
/G1B11: RGB1B11.2, U-RGB1B.9
/G1B12: RGB1B12.2, U-RGB1B.27
/G1B13: RGB1B13.2, U-RGB1B.21
/G1B14: RGB1B14.2, U-RGB1B.18
/G1B15: RGB1B15.2, U-RGB1B.12
/G1C0: RGB1C0.2, U-RGB1C.44
/G1C1: RGB1C1.2, U-RGB1C.50
/G1C2: RGB1C2.2, U-RGB1C.53
/G1C3: RGB1C3.2, U-RGB1C.3
/G1C4: RGB1C4.2, U-RGB1C.41
/G1C5: RGB1C5.2, U-RGB1C.47
/G1C6: RGB1C6.2, U-RGB1C.56
/G1C7: RGB1C7.2, U-RGB1C.6
/G1C8: RGB1C8.2, U-RGB1C.30
/G1C9: RGB1C9.2, U-RGB1C.24
/G1C10: RGB1C10.2, U-RGB1C.15
/G1C11: RGB1C11.2, U-RGB1C.9
/G1C12: RGB1C12.2, U-RGB1C.27
/G1C13: RGB1C13.2, U-RGB1C.21
/G1C14: RGB1C14.2, U-RGB1C.18
/G1C15: RGB1C15.2, U-RGB1C.12
/G2A0: RGB2A0.2, U-RGB2A.44
/G2A1: RGB2A1.2, U-RGB2A.50
/G2A2: RGB2A2.2, U-RGB2A.53
/G2A3: RGB2A3.2, U-RGB2A.3
/G2A4: RGB2A4.2, U-RGB2A.41
/G2A5: RGB2A5.2, U-RGB2A.47
/G2A6: RGB2A6.2, U-RGB2A.56
/G2A7: RGB2A7.2, U-RGB2A.6
/G2A8: RGB2A8.2, U-RGB2A.30
/G2A9: RGB2A9.2, U-RGB2A.24
/G2A10: RGB2A10.2, U-RGB2A.15
/G2A11: RGB2A11.2, U-RGB2A.9
/G2A12: RGB2A12.2, U-RGB2A.27
/G2A13: RGB2A13.2, U-RGB2A.21
/G2A14: RGB2A14.2, U-RGB2A.18
/G2A15: RGB2A15.2, U-RGB2A.12
/G2B0: RGB2B0.2, U-RGB2B.44
/G2B1: RGB2B1.2, U-RGB2B.50
/G2B2: RGB2B2.2, U-RGB2B.53
/G2B3: RGB2B3.2, U-RGB2B.3
/G2B4: RGB2B4.2, U-RGB2B.41
/G2B5: RGB2B5.2, U-RGB2B.47
/G2B6: RGB2B6.2, U-RGB2B.56
/G2B7: RGB2B7.2, U-RGB2B.6
/G2B8: RGB2B8.2, U-RGB2B.30
/G2B9: RGB2B9.2, U-RGB2B.24
/G2B10: RGB2B10.2, U-RGB2B.15
/G2B11: RGB2B11.2, U-RGB2B.9
/G2B12: RGB2B12.2, U-RGB2B.27
/G2B13: RGB2B13.2, U-RGB2B.21
/G2B14: RGB2B14.2, U-RGB2B.18
/G2B15: RGB2B15.2, U-RGB2B.12
/G2C0: RGB2C0.2, U-RGB2C.44
/G2C1: RGB2C1.2, U-RGB2C.50
/G2C2: RGB2C2.2, U-RGB2C.53
/G2C3: RGB2C3.2, U-RGB2C.3
/G2C4: RGB2C4.2, U-RGB2C.41
/G2C5: RGB2C5.2, U-RGB2C.47
/G2C6: RGB2C6.2, U-RGB2C.56
/G2C7: RGB2C7.2, U-RGB2C.6
/G2C8: RGB2C8.2, U-RGB2C.30
/G2C9: RGB2C9.2, U-RGB2C.24
/G2C10: RGB2C10.2, U-RGB2C.15
/G2C11: RGB2C11.2, U-RGB2C.9
/G2C12: RGB2C12.2, U-RGB2C.27
/G2C13: RGB2C13.2, U-RGB2C.21
/G2C14: RGB2C14.2, U-RGB2C.18
/G2C15: RGB2C15.2, U-RGB2C.12
/GSCLK1: J1.2, U-RGB1A.34, U-RGB1B.34, U-RGB1C.34, U-UV1A.34, U-UV1C.34
/GSCLK2: J1.9, U-RGB2A.34, U-RGB2B.34, U-RGB2C.34, U-UV2A.34, U-UV2C.34
/LAT1: J1.6, U-RGB1A.38, U-RGB1B.38, U-RGB1C.38, U-UV1A.38, U-UV1C.38
/LAT2: J1.13, U-RGB2A.38, U-RGB2B.38, U-RGB2C.38, U-UV2A.38, U-UV2C.38
/R1A0: RGB1A0.4, U-RGB1A.43
/R1A1: RGB1A1.4, U-RGB1A.49
/R1A2: RGB1A2.4, U-RGB1A.52
/R1A3: RGB1A3.4, U-RGB1A.2
/R1A4: RGB1A4.4, U-RGB1A.40
/R1A5: RGB1A5.4, U-RGB1A.46
/R1A6: RGB1A6.4, U-RGB1A.55
/R1A7: RGB1A7.4, U-RGB1A.5
/R1A8: RGB1A8.4, U-RGB1A.31
/R1A9: RGB1A9.4, U-RGB1A.25
/R1A10: RGB1A10.4, U-RGB1A.16
/R1A11: RGB1A11.4, U-RGB1A.10
/R1A12: RGB1A12.4, U-RGB1A.28
/R1A13: RGB1A13.4, U-RGB1A.22
/R1A14: RGB1A14.4, U-RGB1A.19
/R1A15: RGB1A15.4, U-RGB1A.13
/R1B0: RGB1B0.4, U-RGB1B.43
/R1B1: RGB1B1.4, U-RGB1B.49
/R1B2: RGB1B2.4, U-RGB1B.52
/R1B3: RGB1B3.4, U-RGB1B.2
/R1B4: RGB1B4.4, U-RGB1B.40
/R1B5: RGB1B5.4, U-RGB1B.46
/R1B6: RGB1B6.4, U-RGB1B.55
/R1B7: RGB1B7.4, U-RGB1B.5
/R1B8: RGB1B8.4, U-RGB1B.31
/R1B9: RGB1B9.4, U-RGB1B.25
/R1B10: RGB1B10.4, U-RGB1B.16
/R1B11: RGB1B11.4, U-RGB1B.10
/R1B12: RGB1B12.4, U-RGB1B.28
/R1B13: RGB1B13.4, U-RGB1B.22
/R1B14: RGB1B14.4, U-RGB1B.19
/R1B15: RGB1B15.4, U-RGB1B.13
/R1C0: RGB1C0.4, U-RGB1C.43
/R1C1: RGB1C1.4, U-RGB1C.49
/R1C2: RGB1C2.4, U-RGB1C.52
/R1C3: RGB1C3.4, U-RGB1C.2
/R1C4: RGB1C4.4, U-RGB1C.40
/R1C5: RGB1C5.4, U-RGB1C.46
/R1C6: RGB1C6.4, U-RGB1C.55
/R1C7: RGB1C7.4, U-RGB1C.5
/R1C8: RGB1C8.4, U-RGB1C.31
/R1C9: RGB1C9.4, U-RGB1C.25
/R1C10: RGB1C10.4, U-RGB1C.16
/R1C11: RGB1C11.4, U-RGB1C.10
/R1C12: RGB1C12.4, U-RGB1C.28
/R1C13: RGB1C13.4, U-RGB1C.22
/R1C14: RGB1C14.4, U-RGB1C.19
/R1C15: RGB1C15.4, U-RGB1C.13
/R2A0: RGB2A0.4, U-RGB2A.43
/R2A1: RGB2A1.4, U-RGB2A.49
/R2A2: RGB2A2.4, U-RGB2A.52
/R2A3: RGB2A3.4, U-RGB2A.2
/R2A4: RGB2A4.4, U-RGB2A.40
/R2A5: RGB2A5.4, U-RGB2A.46
/R2A6: RGB2A6.4, U-RGB2A.55
/R2A7: RGB2A7.4, U-RGB2A.5
/R2A8: RGB2A8.4, U-RGB2A.31
/R2A9: RGB2A9.4, U-RGB2A.25
/R2A10: RGB2A10.4, U-RGB2A.16
/R2A11: RGB2A11.4, U-RGB2A.10
/R2A12: RGB2A12.4, U-RGB2A.28
/R2A13: RGB2A13.4, U-RGB2A.22
/R2A14: RGB2A14.4, U-RGB2A.19
/R2A15: RGB2A15.4, U-RGB2A.13
/R2B0: RGB2B0.4, U-RGB2B.43
/R2B1: RGB2B1.4, U-RGB2B.49
/R2B2: RGB2B2.4, U-RGB2B.52
/R2B3: RGB2B3.4, U-RGB2B.2
/R2B4: RGB2B4.4, U-RGB2B.40
/R2B5: RGB2B5.4, U-RGB2B.46
/R2B6: RGB2B6.4, U-RGB2B.55
/R2B7: RGB2B7.4, U-RGB2B.5
/R2B8: RGB2B8.4, U-RGB2B.31
/R2B9: RGB2B9.4, U-RGB2B.25
/R2B10: RGB2B10.4, U-RGB2B.16
/R2B11: RGB2B11.4, U-RGB2B.10
/R2B12: RGB2B12.4, U-RGB2B.28
/R2B13: RGB2B13.4, U-RGB2B.22
/R2B14: RGB2B14.4, U-RGB2B.19
/R2B15: RGB2B15.4, U-RGB2B.13
/R2C0: RGB2C0.4, U-RGB2C.43
/R2C1: RGB2C1.4, U-RGB2C.49
/R2C2: RGB2C2.4, U-RGB2C.52
/R2C3: RGB2C3.4, U-RGB2C.2
/R2C4: RGB2C4.4, U-RGB2C.40
/R2C5: RGB2C5.4, U-RGB2C.46
/R2C6: RGB2C6.4, U-RGB2C.55
/R2C7: RGB2C7.4, U-RGB2C.5
/R2C8: RGB2C8.4, U-RGB2C.31
/R2C9: RGB2C9.4, U-RGB2C.25
/R2C10: RGB2C10.4, U-RGB2C.16
/R2C11: RGB2C11.4, U-RGB2C.10
/R2C12: RGB2C12.4, U-RGB2C.28
/R2C13: RGB2C13.4, U-RGB2C.22
/R2C14: RGB2C14.4, U-RGB2C.19
/R2C15: RGB2C15.4, U-RGB2C.13
/SCLK1: J1.5, U-RGB1A.37, U-RGB1B.37, U-RGB1C.37, U-UV1A.37, U-UV1C.37
/SCLK2: J1.12, U-RGB2A.37, U-RGB2B.37, U-RGB2C.37, U-UV2A.37, U-UV2C.37
/SIN1: J1.3, U-RGB1A.36
/SIN2: J1.10, U-RGB2A.36
/SOUT1: J1.7, U-RGB1C.7
/SOUT2: J1.14, U-RGB2C.7
/UV1A0: U-UV1A.42, UV1A0.1
/UV1A1: U-UV1A.48, UV1A1.1
/UV1A2: U-UV1A.51, UV1A2.1
/UV1A3: U-UV1A.1, UV1A3.1
/UV1A4: U-UV1A.39, UV1A4.1
/UV1A5: U-UV1A.45, UV1A5.1
/UV1A6: U-UV1A.54, UV1A6.1
/UV1A7: U-UV1A.4, UV1A7.1
/UV1A8: U-UV1A.32, UV1A8.1
/UV1A9: U-UV1A.26, UV1A9.1
/UV1A10: U-UV1A.17, UV1A10.1
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

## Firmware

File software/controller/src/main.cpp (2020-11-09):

/* main.cpp

Copyright 2020 Samuel B. Powell
samuel.powell@uq.edu.au

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
THE SOFTWARE IS PROVIDED "AS IS", WITHOUT WARRANTY OF ANY KIND, EXPRESS OR
IMPLIED, INCLUDING BUT NOT LIMITED TO THE WARRANTIES OF MERCHANTABILITY,
FITNESS FOR A PARTICULAR PURPOSE AND NONINFRINGEMENT. IN NO EVENT SHALL THE
AUTHORS OR COPYRIGHT HOLDERS BE LIABLE FOR ANY CLAIM, DAMAGES OR OTHER
LIABILITY, WHETHER IN AN ACTION OF CONTRACT, TORT OR OTHERWISE, ARISING FROM,
OUT OF OR IN CONNECTION WITH THE SOFTWARE OR THE USE OR OTHER DEALINGS IN THE
SOFTWARE.
*/

#include "Arduino.h"

#include "TLC5955.h"
#include "scpi.h"

#include <array>

//use Serial for USB, Serial1 for UART
#define SER Serial

#define SYSTEM_HELP                                                                    \
  "UVTV System Help\r\n"                                                               \
  "  This system uses the SCPI standard for communication and control.\r\n"            \
  "  Send any of the following commands followed by ENTER to execute them.\r\n"        \
  "  Commands are not case-sensitive, but have short and long forms. The short \r\n"   \
  "  form is indicated by capitals. [] indicate optional parts.\r\n"                   \
  "  E.g. STATus:ERRor[:NEXT]?  can be executed by entering any of the following:\r\n" \
  "    \"STAT:err?\" or \"status:error?\" or \"STATus:error:next?\" etc.\r\n"          \
  "  N.B. Many of the mandated commands are not implemented on this system.\r\n"       \
  "\r\n"                                                                               \
  "  Image data is specified in a row-major interleaved format. Each pixel is\r\n"     \
  "  5 16-bit values: R,G,B,V,UV where 0000 is off and FFFF is on. Additionally,\r\n"  \
  "  each color channel has a 3-bit maximum current and 7-bit brightness, and\r\n"     \
  "  each pixel has a 7-bit dot correction, all of which control the LED drive\r\n"    \
  "  current. See the TLC5955 datasheet for more information.\r\n"                     \
  "  Binary data is encoded using the SCPI block format: #<d><len><data>, where\r\n"   \
  "    <d> and <len> are ASCII encoded decimal numbers,\r\n"                           \
  "    <d> is a single decimal digit, the number of digits in <len>, and\r\n"          \
  "    <len> is the number of bytes in <data>."                                        \
  "\r\n\r\nCommands:\r\n"

//TODO:
// - address translation will need modification to support panels wider than 12

constexpr uint32_t PANEL_WIDTH = 12;
constexpr uint32_t PANEL_HEIGHT = 8;
constexpr uint32_t PANEL_CHANNELS = 5;
constexpr uint32_t PANEL_DIMS[3] = {PANEL_HEIGHT, PANEL_WIDTH, PANEL_CHANNELS};

constexpr size_t PANEL_CHIPS = 10;
constexpr size_t NUM_LEDS = PANEL_CHIPS * TLC5955::NUM_LEDS;

constexpr int PIN_GCLK = 20, PIN_SCLK = 14, PIN_MOSI = 11, PIN_MISO = 12, PIN_LATCH = 10;

constexpr size_t SER_LEN = 8;
constexpr char *ROM_SER = 0; //null terminated string, at most 8 bytes long
constexpr uint32_t *ROM_BR = (uint32_t *)8;
constexpr void *ROM_CTRL = (void*)32;

const char *SCPI_IDN1 = "\"Samuel Powell\""; //Manufacturer
const char *SCPI_IDN2 = "UVTV";              //Model
static char SCPI_IDN3[SER_LEN+1] = {0}; //Serial #, read from EEPROM but still needs global allocation
const char *SCPI_IDN4 = "2020-11-02";                 //Revision

bool echo = true, enabled = false;

template <typename T, size_t N>
constexpr size_t alen(const T (&arr)[N]) { return N; }

//LED globals
TLC5955 leds(KINETISK_SPI0);
uint8_t pwm_buffer[PANEL_CHIPS * TLC5955::PWM_BUFFER_SIZE];
uint8_t ctrl_buffer[PANEL_CHIPS * TLC5955::CTRL_BUFFER_SIZE];

/* PIXEL -> LED ADDRESS TRANSLATION

We receive pixels in a row-major interleaved format (y, x, c) with dimensions
 (PANEL_HEIGHT, PANEL_WIDTH, 5).
The LED driver chips, however, each control a rectangular patch of 48 LEDs.
The RGB chips each control a 4x4x3 patch while the VUV chips control 4x6x2.
The chips are daisy chained in groups of 5: RGB-VUV-RGB-VUV-RGB
*/

size_t rgb_chips[] = {0, 2, 4, 5, 7, 9}; // RGB chip indices, terminated in (size_t)(-1)
size_t uv_chips[] = {1, 3, 6, 8};        // UV chip indices, terminated in (size_t)(-1)
size_t ctrl_addr(size_t chip)
{
  return chip * TLC5955::CTRL_BUFFER_SIZE;
}

//give the index of the RGB LED at (y,x,c) in a single chain
size_t pixel_addr_rgb(size_t y, size_t x, size_t c)
{
  size_t cy = y / 4, cx = x / 4; //chip coordinates
  y -= 4 * cy;
  x -= 4 * cx; //pixel coordinates in the chip
  return cy * (5 * 0x30) + cx * 0x60 + y * 12 + x * 3 + c;
}

//give the index of the V/UV LED at (y,x,c) in a single chain
//in this case, c = 0: V, 1: UV
size_t pixel_addr_vuv(size_t y, size_t x, size_t c)
{
  static size_t lut[] = {
      0, 1, 3, 6, 7, 9,  //V indices along the top row
      2, 4, 5, 8, 10, 11 //UV indices along the top row
  };
  size_t cy = y / 4, cx = x / 6; //chip coordinates
  y -= 4 * cy;
  x -= 6 * cx; //pixel coordinates in the chip
  return cy * (5 * 0x30) + cx * 0x60 + 0x30 + y * 12 + lut[c * 6 + x];
}

//give the index of the first LED of the chip that covers pixel (y,x) given
// the channel c
size_t pixel_addr(size_t y, size_t x, size_t c)
{
  if (c < 3)
    return pixel_addr_rgb(y, x, c);
  else
    return pixel_addr_vuv(y, x, c - 3);
}

//global look-up table for reordering pixels
constexpr size_t lut_addr(size_t y, size_t x, size_t c)
{
  return c + PANEL_CHANNELS * (x + PANEL_WIDTH * y);
}

size_t pixel_addr_lut[lut_addr(PANEL_HEIGHT, 0, 0)];

void init_pixel_addr_lut()
{
  for (size_t y = 0; y < PANEL_HEIGHT; ++y)
    for (size_t x = 0; x < PANEL_WIDTH; ++x)
      for (size_t c = 0; c < PANEL_CHANNELS; ++c)
        pixel_addr_lut[lut_addr(y, x, c)] = pixel_addr(y, x, c);
}

/* SCPI Commands */
constexpr size_t SCPI_INPUT_BUFFER_SIZE = 1024;
constexpr size_t SCPI_ERROR_QUEUE_SIZE = 4;


namespace System
{ //use a namespace to aid code browsing
scpi_result_t Help(scpi_t *ctx);
scpi_result_t Prog(scpi_t *ctx);
scpi_result_t Ser(scpi_t *ctx);
scpi_result_t SerQ(scpi_t *ctx);
scpi_result_t ErrAllQ(scpi_t *ctx);
scpi_result_t CommEcho(scpi_t *ctx);
scpi_result_t CommEchoQ(scpi_t *ctx);
} // namespace System

namespace Display
{
scpi_result_t GeomQ(scpi_t *ctx);

scpi_result_t Mode(scpi_t *ctx);
scpi_result_t ModeQ(scpi_t *ctx);

scpi_result_t Maxc(scpi_t *ctx);
scpi_result_t MaxcQ(scpi_t *ctx);

scpi_result_t Bri(scpi_t *ctx);
scpi_result_t BriQ(scpi_t *ctx);

scpi_result_t Dotc(scpi_t *ctx);
scpi_result_t DotcQ(scpi_t *ctx);

scpi_result_t DotcAll(scpi_t *ctx);
scpi_result_t DotcAllQ(scpi_t *ctx);

scpi_result_t CurrQ(scpi_t *ctx);

scpi_result_t Save(scpi_t *ctx);
scpi_result_t Load(scpi_t *ctx);

scpi_result_t Pwm(scpi_t *ctx);
scpi_result_t PwmQ(scpi_t *ctx);

scpi_result_t PwmAll(scpi_t *ctx);
scpi_result_t PwmAllQ(scpi_t *ctx);

scpi_result_t En(scpi_t *ctx);
scpi_result_t EnQ(scpi_t *ctx);

scpi_result_t Refr(scpi_t *ctx);

scpi_result_t SPIFreq(scpi_t *ctx);
scpi_result_t SPIFreqQ(scpi_t *ctx);

scpi_result_t LutQ(scpi_t *ctx);
} // namespace Display

scpi_command_t scpi_commands[] = { //{pattern, callback, tag}
    //Standard commands
    SCPI_CMDS_BASIC,
    //System
    {"HELP", System::Help, 0},
    {"SYSTem:HELP:HEADers?", System::Help, 1},
    {"SYSTem:PROGram", System::Prog, 0},
    {"SYSTem:SERial", System::Ser, 0},
    {"SYSTem:SERial?", System::SerQ, 0},
    {"SYSTem:ERRor:ALL?", System::ErrAllQ, 0},
    {"SYSTem:COMMunicate:ECHO", System::CommEcho, 0},
    {"SYSTem:COMMunicate:ECHO?", System::CommEchoQ, 0},
    {"DISPlay[:ENable]", Display::En, 0},
    {"DISPlay[:ENable]?", Display::EnQ, 0},
    {"DISPlay:MODE", Display::Mode, 0},
    {"DISPlay:MODE?", Display::ModeQ, 0},
    {"DISPlay:GEOMetry?", Display::GeomQ, 0},
    {"DISPlay:MAXCurrent", Display::Maxc, 0},
    {"DISPlay:MAXCurrent?", Display::MaxcQ, 0},
    {"DISPlay:BRIghtness", Display::Bri, 0},
    {"DISPlay:BRIghtness?", Display::BriQ, 0},
    {"DISPlay:DOTCorrect", Display::Dotc, 0},
    {"DISPlay:DOTCorrect?", Display::DotcQ, 0},
    {"DISPlay:DOTCorrect:ALL", Display::DotcAll, 0},
    {"DISPlay:DOTCorrect:ALL?", Display::DotcAllQ, 0},
    {"DISPlay:CURRent?",Display::CurrQ, 0},
    {"DISPlay:SAVE", Display::Save, 0},
    {"DISPlay:LOAD", Display::Load, 0},
    {"DISPlay:PWM", Display::Pwm, 0},
    {"DISPlay:PWM?", Display::PwmQ, 0},
    {"DISPlay:PWM:ALL", Display::PwmAll, 0},
    {"DISPlay:PWM:ALL?", Display::PwmAllQ, 0},
    {"DISPlay:SPIFrequency", Display::SPIFreq, 0},
    {"DISPlay:SPIFrequency?", Display::SPIFreqQ, 0},
    {"DISPlay:REFResh", Display::Refr, 0},
    {"DISPlay:LUT?", Display::LutQ, 0},
    SCPI_CMD_LIST_END};

scpi_help_t scpi_help[] = {
    {"HELP", "Print this help message"},
    {"SYSTem:HELP:HEADers?", "List all commands"},
    SCPI_HELP_BASIC,
    {"SYSTem:ERRor:ALL?", "List all current errors"},
    {"SYSTem:PROGram", "Reboot into bootloader for programming"},
    {"SYSTem:SERial?", "The device serial number, as reported by *IDN?"},
    {"SYSTem:COMMunicate:ECHO[?] ON|OFF", "Enable serial echo"},
    {"DISPlay[:ENable][?]", "Turn panel on or off"},
    {"DISPlay:GEOMetry?", "Return HEIGHT,WIDTH,CHANNELS of the panel"},
    {"DISPlay:MODE[?]", "5-bit Function Control register. Accepts a number or a list of named options:\r\n    Dsprpt, Tmgrst, Rfresh, Espwm, Lsdvlt\r\n  D,E is probably what you want."},
    {"DISPlay:MAXCurrent[?]", "R,G,B,V: 4x 3-bit maximum current code. UV uses the same max current as V."},
    {"DISPlay:BRIghtness[?]", "R,G,B,V: 4x 7-bit brightness code. UV uses the same brightness as V."},
    {"DISPlay:DOTCorrect[?]", "y,x,c[,DC]: 7-bit dot correct code for LED at (y,x,c)"},
    {"DISPlay:DOTCorrect:ALL[?]", "All dot correct codes, binary encoded each in 1 byte."},
    {"DISPlay:SAVE", "Save SPIFreq, MODE, MAXCurrent, and DOTCorrect values"},
    {"DISPlay:LOAD", "Load SPIFreq, MODE, MAXCurrent, and DOTCorrect values"},
    {"DISPlay:PWM[?]", "y,x,c[,PWM]: 16-bit PWM code for LED at (y,x,c)"},
    {"DISPlay:PWM:ALL[?]", "All PWM codes, binary encoded each in 2 bytes."},
    {"DISPlay:CURRent?", "Estimate current required to display image."},
    {"DISPlay:SPIFrequency[?]", "f: set frequency, returns actual."},
    {"DISPlay:REFResh", "(Re)send PWM codes to panel."},
    SCPI_HELP_LIST_END};

size_t scpi_write(scpi_t *ctx, const char *data, size_t len)
{
  return SER.write(data, len);
}

void restart()
{
  //ARM Cortex-M: write SYSRESETREQ to NVIC Application Interrupt and Reset Control
  *((uint32_t *)0xE000ED0C) = 0x5FA0004;
}

scpi_result_t scpi_reset(scpi_t *ctx)
{
  SCPI_ResultCharacters(ctx, "**RESET**", 9);
  SER.flush();
  delay(100);
  restart();
  return SCPI_RES_OK;
}

int scpi_error(scpi_t *ctx, int_fast16_t err)
{
  if (err != SCPI_ERROR_NO_ERROR)
    SCPI_ResultCharacters(ctx, "**ERROR**", 9);
  return 0;
}

scpi_interface_t scpi_interface =
    {scpi_error, scpi_write, nullptr, nullptr, scpi_reset};

char scpi_input_buffer[SCPI_INPUT_BUFFER_SIZE];

scpi_error_t scpi_error_queue[SCPI_ERROR_QUEUE_SIZE];

scpi_t scpi_context;

scpi_result_t System::Help(scpi_t *ctx)
{
  switch (SCPI_CmdTag(ctx))
  {
  case 0: //HELP
    SER.print(SYSTEM_HELP);
    for (auto *help = scpi_help; help->syntax != nullptr; ++help)
    {
      SER.printf("%s\r\n  %s\r\n", help->syntax, help->description);
    }
    break;
  case 1: //SYSTem:HELP:HEADers?
    for (auto *help = scpi_help; help->syntax != nullptr; ++help)
    {
      SER.println(help->syntax);
    }
    break;
  default:
    return SCPI_RES_ERR;
  }
  return SCPI_RES_OK;
}

scpi_result_t System::ErrAllQ(scpi_t *ctx)
{
  //comma seperated list of all errors. always returns at least 1 item
  scpi_error_t err;
  SCPI_ErrorPop(ctx, &err);
  SCPI_ResultError(ctx, &err);
  while (SCPI_ErrorPop(ctx, &err) && err.error_code != SCPI_ERROR_NO_ERROR)
  {
    SCPI_ResultError(ctx, &err);
  }
  return SCPI_RES_OK;
}

scpi_result_t System::Prog(scpi_t *ctx)
{
  _reboot_Teensyduino_();
  return SCPI_RES_OK;
}
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

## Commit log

2019-12-02 initial commit -- KiCAD files
    [UVTV v1 BOM.xlsx, UVTV-B.Cu.gbr, UVTV-B.Mask.gbr, UVTV-B.Paste.gbr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]
2019-12-02 add teensy-carrier board
    [teensy-carrier.kicad_pcb, teensy-carrier.sch]
2019-12-03 add teensy.lib
2019-12-03 work on teensy-carrier
    [UVTV-control-B_Cu.gbr, UVTV-control-B_Mask.gbr, UVTV-control-B_SilkS.gbr, UVTV-control-Edge_Cuts.gbr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]
2019-12-20 fix reversed wiring
    [teensy-carrier.kicad_pcb, teensy-carrier.sch]
2020-01-08 fix pin ordering, use terminal blocks instead of pin headers for power entry/supply
    [teensy-carrier.kicad_pcb, teensy-carrier.sch]
2020-01-08 archive v1 gerbers, generate v2 gerbers
    [UVTV-control.drl, teensy-carrier-B_Cu.gbr, teensy-carrier-B_Mask.gbr, teensy-carrier-B_SilkS.gbr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]
2020-12-21 Add board 2 data 0
2020-12-21 add board 2 data/1
2020-12-21 Add board 2 data/2
2020-12-21 add 'board 2 data' summary info and README
2021-01-28 Add 3D models
    [LED box bracket.ipt, LED box bracket.stl, LED box top.ipt, LED box top.stl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]
2021-02-22 Add OpenSCAD models to replace Inventor.
    [baffle.scad, led_box.scad]
2023-01-20 refactor test_panel.py to improve safety
    - explicit operating modes rather than boolean flags (reset_config was dangerous!)
    - check for files before overwriting them (reset_config was dangerous!)
    - check for serial number mismatch between board & config file before programming
    - add 'download' mode to pull config data from the board
    - add 'test-board' mode to test config data stored on the board
